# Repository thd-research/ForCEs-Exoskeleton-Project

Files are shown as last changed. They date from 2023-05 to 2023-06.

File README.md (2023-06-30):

# ForCEs-Exoskeleton-Project
Internal Project for the development of a lower-limb active exoskeleton at the Deggendorf Institute of Technology

## Description
The goal of this project is the design and development of an exoskeleton that can be worn with higher levels of acceptance
from patients. In particular, the actuator has a unique four-bar-linkage design, with a conventional belt-and-pulley drive
that allows it to be back driveable. 
The Control System of the exoskeleton relies on the operation of multiple interfaces, mainly a core running on a central processor, 
in this case, a portable Raspberry Pi 4 model B (4 Gb). Arduino Microcontrollers were used for Data Acquisition and ADC.
No specific HMI exists for the use and operation of the exoskeleton. Since an ODrive v3.4 controller is used for the motor control,
most testing and interactions have been achieved through CLI and basic python scripts.
The support structure is created with topology optimization and a prototype was assembled with powder printed parts.
The EMG and Motion Capture Data can be visualized with Software such as EMGandMotionTools by Cometa.

## Structure
- python scripts for:
-- the computation with four-bar-linkage 
-- basic odrive control
- arduino codes for sensor input and control
- cad files for the actuator construction details
- EMG and Motion Capture data 

## Goal of this Repository
To complement the publication titled "Design and Development of a knee rehabilitation exoskeleton with four-bar linkage actuation", so that the experimental trials, as well as results are made available and can be reproduced independently. This work has been completed by several researchers at the DIT and crediting us for any use of the material here would be very much appreciated.
For the image/build file for the Raspberry Pi and additional work with AI Gait recognition, please contact us.

Further organisation information under: https://zaf.th-deg.de/public/project/201

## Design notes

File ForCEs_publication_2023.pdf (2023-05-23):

## Design and Development of a knee rehabilitation exoskeleton with four-bar linkage actuation

C. Y. Aubeeluck¹
, S. Kolbl ¨

1

, D. Dobriborsci¹

and W. Aumer¹

Abstract— In this paper, the design of a lower limb active exoskeleton for rehabilitation purposes is discussed. Active exoskeletons provide the additional required force for motion and gait correction, especially for patients who have suffered from limb impairment. The development was carried out taking into account sensor input for the control system. A Finite-State Machine (FSM) enables the different motions which rely on the data from the torque and acceleration sensors. To replicate the anatomical knee rotation, a four-bar linkage was modelled and integrated in the actuator drive. For this project, a prototype was created using Additive Manufacturing Processes (AMP). The prototype is part of the ’ForCEs’ project at Deggendorf Institute of Technology (DIT) and was tested at an experimental stage for an initial set of results.

I. INTRODUCTION

A variety of conditions results in the impairment of the knee joint, namely chronic illnesses such as cerebral palsy and arthritis, for which the most common treatment is physiotherapy [1]. In modern physiotherapy, active exoskeletons, such as MINDWALKER [2], ReWalk [3], and HAL [4], are mechanized wearables that can be used to assist in rehabilitation. With the use of innovative actuating technologies, and novel material manufacturing processes, researchers have come up with exoskeletons that require the least assistance from medical experts. For rehabilitation, the ‘MINDWALKER’ uses a compact and compliant series elastic actuator with a Brushless DC motor (BLDC). However, despite BLDCs being the most popular actuation choice, bulkiness and low acceptability with patients remain an issue. Another feature is the intent detection for disabled patients. The ‘ReWalk’ exoskeleton consists of a remote control as its input, while the ‘HAL’ by Cyberdyne is the only assistance device with Electromyography (EMG) sensors. While the surface-EMG sensors’ feasibility has been verified, there are still limitations such as noise due to poor adhesion. Furthermore, surface-EMG and EEG electrodes must be adhered to the patient for best results, which drastically decreases their practical usage for daily life applications. Table I summarizes the key elements of the state-of-the-art exoskeletons.

Exoskeleton | Sensing Method | Actuating Method | Joint Type
MINDWALKER ReWalk HAL | IMU Tilt and Torque EMG | linear actuator dc motor dc motor | single-pivot -single-pivot

TABLE I: State of the art exoskeletons (IMU: Inertial Measurement Unit).

1Deggendorf Institute of Technology, TC Cham, 21 Badstraße, 93413 Cham, Germany chandra.aubeeluck@th-deg.de

Based on the review of exoskeletons’ sensors, IMU’s alone serve little purpose in intent detection as they cannot distinguish between the person’s and the actuator’s motion. However, if a secondary or more sensors’ data are combined, an estimation can be obtained. In the ForCEs project [5], a combination of IMU’s and torque sensor has been implemented. This reduces the inconvenience with surface-EMG electrodes. Furthermore, the resistance in motion can be monitored effectively, as opposed to an EMG only solution, where specific muscular activity has to be categorized. At the same time, an adaptive position is generated since the IMU and an angle sensor monitor the leg velocity changes.

By not using a single-pivot joint, the polycentric rotation of the knee, due to the roll and glide motion, has been replicated. One possibility to replicate the anatomical knee rotation is mentioned in [6], where a four-bar linkage approach is introduced. In our case, a similar mechanism has been devised which closer resembles the ligaments inside the knee. These are the Anterior and Posterior Cruciate Ligaments (ACL and PCL) [7]. The femur and tibia bones are the two additional links. The changing centre of rotation is demonstrated in Figure 1. Another key aspect is the use of AMP which improves the form, fit and function of the support structure and actuator. With a backdrivable speed reduction mechanism, the use of a clutch system is eliminated, which makes the actuator lighter.

After a short introduction, the limitations of existing designs are discussed in Section II. Afterwards, the modelling and design of proposed relevant solutions are explained in Section III. Next, in Section IV, an analysis of the implemented solutions is performed and discussed. At the end of Section IV, the obtained results are evaluated. A general emphasis is laid on the overall design concept including the control system, with particular attention to the actuator and four-bar linkage design.

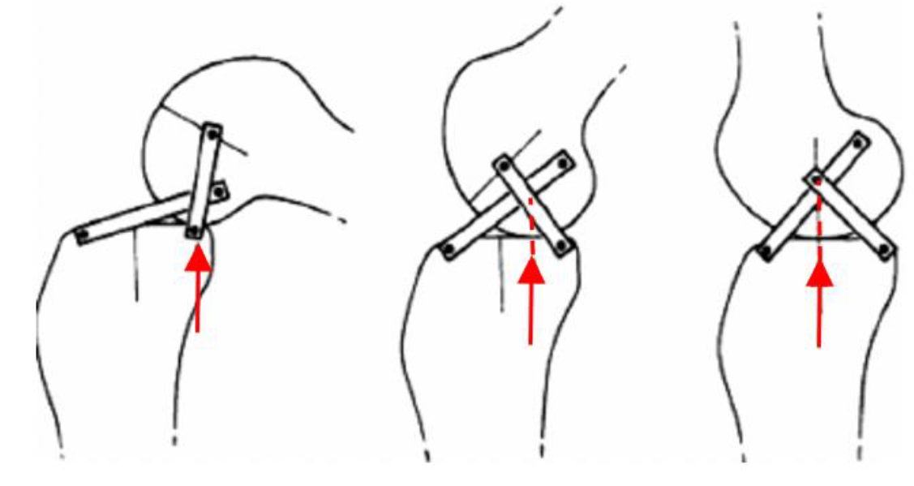
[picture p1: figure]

Fig. 1: Four-bar linkage in the knee. The shifting instantaneous centre of rotation (ICR) is indicated by the red arrow.

II. PROBLEM STATEMENT

The four-bar linkage provides a more adaptive rotation of the actuator joint, given the fact that the axis of rotation of the knee is not the same for every person. A proposed solution is aligning the ICR of the actuator and that of the knee by using parts made by AMP for lightweight supports that conform to the leg profile. An improved control algorithm with torque sensors and IMUs would overcome the current limitations and requirements with existing intent detection means. The extent to which this is resolved is discussed in this paper. While the four-bar linkage provides a more adapted solution, it also introduces the problem of irregular force output in which there is a reduction of up to 40 % of the input force. This is further described in [6]. By knowing the exact torque requirements for each angular position of the knee, the output torque can be adjusted, by varying the torque setpoint. While this is computationally not costly, it still requires an onboard online programming for the estimation of the output torque with respect to the input torques, and gait model torque. A lightweight control structure is thus desired, in which a complete modelling of the exoskeleton is simulated.

III. DESIGN OF CONTROL SYSTEM AND PROTOTYPE

The design for the complete exoskeleton was divided into four parts, namely the structural support, actuators, sensors, and the control system. Using the MSC Adams simulation software [8], a multibody simulation (MBS) at the musculoskeletal level was generated. To obtain the profile of the lower limbs in the sagittal plane, the Opti-Track System was used, where markers placed on the body gives the position of the upper and lower legs. From this, the support structure was developed in several stages starting with a simple element which was enhanced through topology-optimization.

A. Control System Design

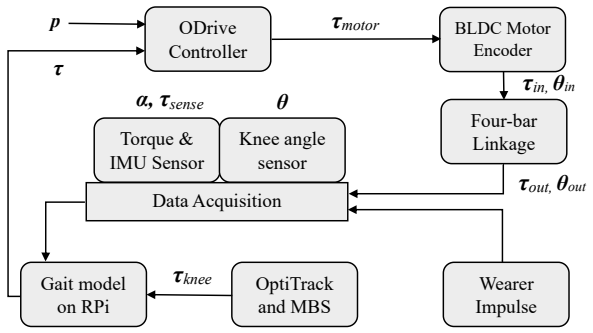
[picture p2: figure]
ODrive Controller; BLDC Motor Encoder; Four-bar Linkage; Wearer Impulse; OptiTrack and MBS; Gait model on RPi; Torque & IMU Sensor; Knee angle sensor; Data Acquisition; τmotor; τin, θin; τout, θout; α, τsense; τknee

Fig. 2: Representation of the exoskeleton Control System.

The components of the control system are illustrated in Figure 2, in which, τ is the torque, α is the tangential acceleration, and θ is the angle of the knee. Further torque variables are τknee, which is the knee required torque according to the gait model and τsense, which is sensed torque. In addition, τmotor is the motor torque, τin is the four-bar linkage input torque at θin and τout is the output torque. The main input variable is designated as the position vector of the motor, p, which is the primary input to a proportional–integral–derivative (PID) controller, where the acceleration is related to the current or torque setpoint, Id of the motor and the voltage Vmotor varies the duty cycle, thus, the motor velocity p˙. This is achieved through the ODrive BLDC Motor Controller [9].

B. Four-bar linkage mechanism

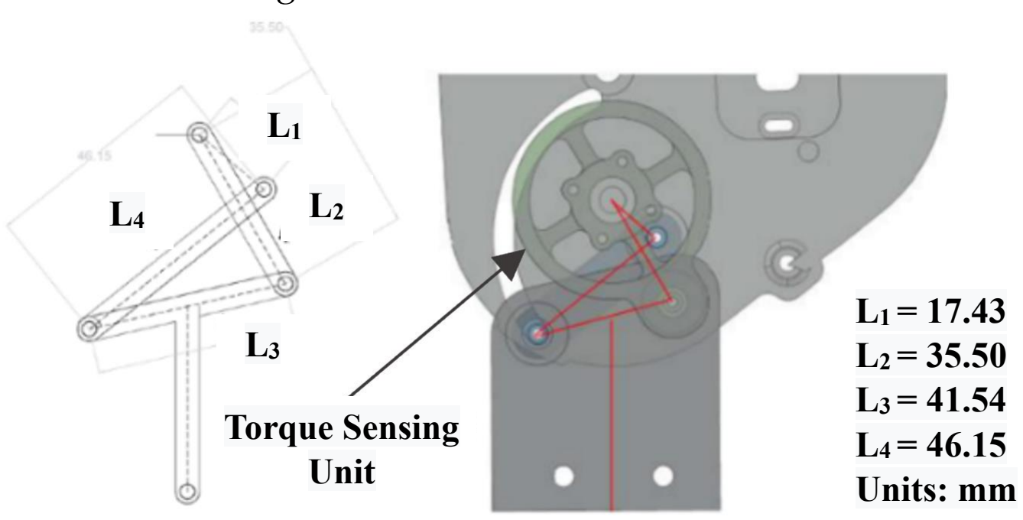
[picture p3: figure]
L1 = 17.43 L2 = 35.50 L3 = 41.54 L4 = 46.15 Units: mm; Torque Sensing Unit

Fig. 3: Four-bar linkage design: dimensions and integration.

The positions and the ratio of the lengths for the knee cruciate ligaments were taken based on the data from [10]. Breaking down the four-bar design, Figure 3 shows the obtained dimensions and design for the four-bar linkage integration. A free-body diagram (FBD) describes the forces in each link, including the relation between the input and output link. The base of the actuator serves as the fixed link L1, which is offset by 40o
to the horizontal. The variations in angular positions are determined by the Freudenstein Equations [11]. The angular range of motion for the input θin, defined by the input or crank link L2, ranges from 20o to 90o
. The output shank connects to link L3 and its rotation θout, relative to the vertical, ranges from 0

o

to 110o
. Link L4
is referred to as the follower, as it determines the path of the output link L3. Link L2 is replaced by a torque sensing element, specifically designed to determine the effective torque input to the four-bar linkage. The forces are distributed in the four links, thus maximizing the permissible peak force acting the torque sensing element, as opposed to the torque sensing element directly transmitting the force to the shank link. In the Autodesk Inventor analysis, the forces are taken from the FBD of the four-bar linkage.

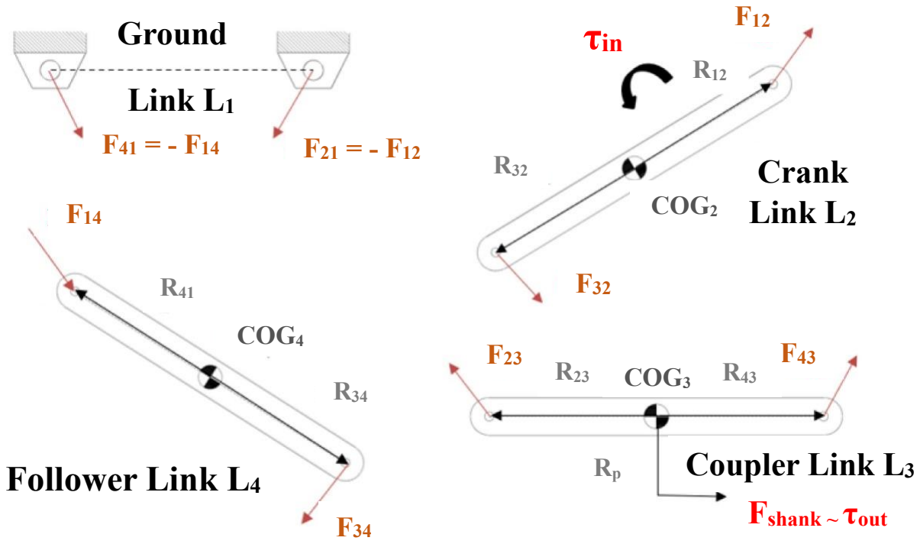
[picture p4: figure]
Ground; Link L1; Follower Link L4; Coupler Link L3; Fshank ~ τout; Crank Link L2 COG2; COG3; COG4; τin

Fig. 4: FBD of four bars for single link analysis.

Figure 4 illustrates each link of the mechanism, clearly showing the fixed Ground L1 and the output force Fshank on the Link L3. The vector quantities Rijxy represent the distance from the Centre of Gravity (COG) and orientation of the links. From the FBD, the forces are resolved at static equilibrium to obtain Equation 1.

Fout = A

−1
- Fin | (1)

where the 8

th element of the (9×1) vector matrix Fout is the force acting on the shank, which is equivalent to the shank torque. Vector matrix Fin contains the elements of the input forces, which in this case is the input torque on the crank link L2 as the 3

rd element. The matrix A is represented in Equation 2. C is the shank length, which is 150 mm. As such, the input and output torques for the linkage are vectors which varies with the angular position. This relation is shown in Figure 5 as the actual torque output with respect

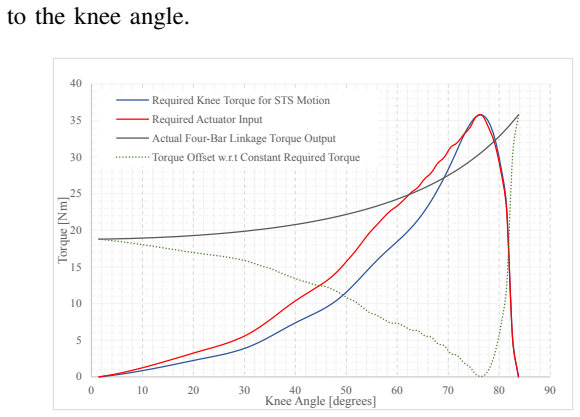
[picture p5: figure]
to the knee angle.; Torque [Nm]; Knee Angle [degrees]; Required Knee Torque for STS Motion; Required Actuator Input; Actual Four-Bar Linkage Torque Output

Torque Offset w.r.t Constant Required Torque

Fig. 5: Torque output from four-bar linkage and offset with respect to Sit-to-Stand (STS) Motion.

From Equation 2, a relation τout = g(τin; θin) is obtained. By iterating the range of torque values with a resolution of 1 Nm, for each knee angle, a difference x exists, which is used in the computation of the actual motor input torque using Equation 3.

τmotor = τout × (

1 + x
100
) | (3)

where
x = τin − τsense | (4)

Equation 4 and its parameters are explained further in section IV. The function g(τin; θin) is dependent on the Freudenstein calculation which is approximated by non-linear curve fitting to obtain

G(θin) = −0.0064θ

2
in + 2.01θin − 37.15 (5)

The required output torque is mapped by the difference e between the output torque τout and the required torque for each gait τknee which varies with the angular positions of the knee. This is represented as the torque offset in Figure
5. The required knee torque τknee is part of the gait model which is represented by a dataset. For this project, the data is retrieved from a CSV file and are operated on as numpy arrays. This allows onboard computation to be performed during the exoskeleton motion. With the required torque for each angular position known, the difference e is determined by first setting the input torque to the peak required torque. In this particular case, the peak required torque is 35 Nm and occurs at knee angle θ = 85o
. The required actuator input τmotor is determined using Equation 3. This is represented in Figure 5 as the required actuator input, where due to the four-bar linkage, in the range 20o < θ < 90o
, the required
actuator torque is decreased to the required knee torque to minimize the torque offset. Within that range, the required torque input is decreased by up to 53 % as shown by the torque offset curve.

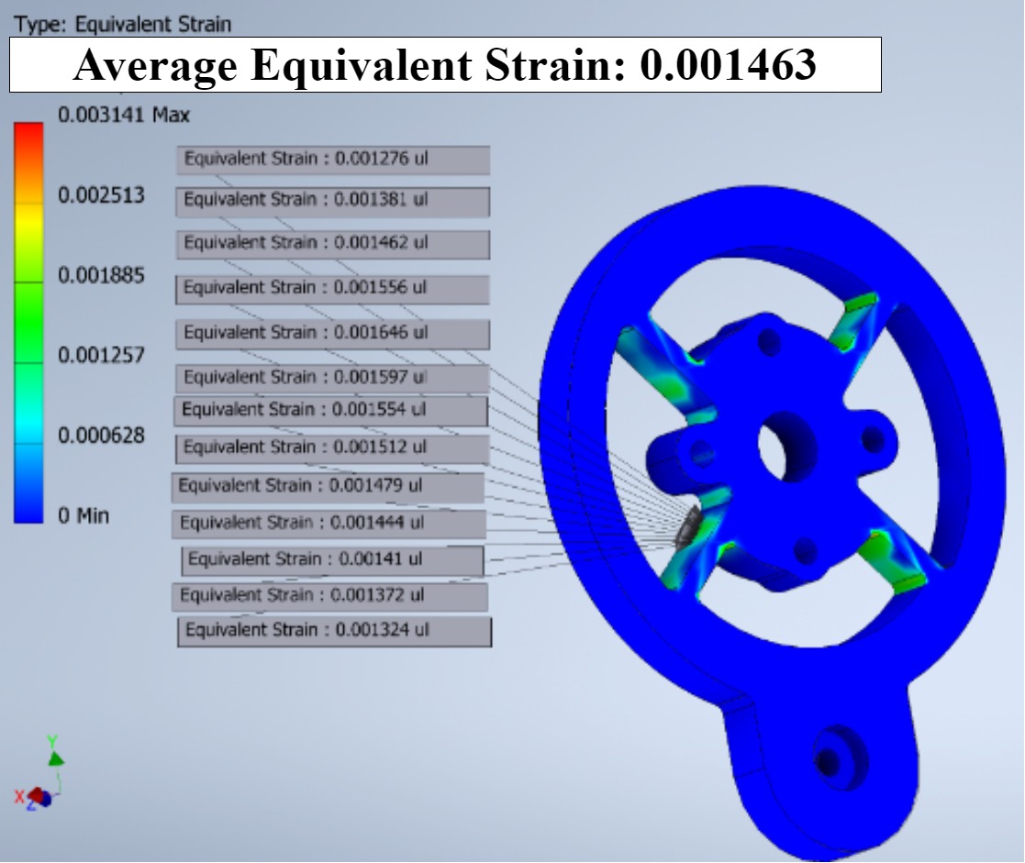
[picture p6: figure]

Fig. 6: FEA analysis on the torque sensing element.

For the torque sensing element, Aluminum 7075 alloy was chosen for its good elastic and yield strength properties. Figure 6 illustrates the Finite Element Analysis (FEA) on the torque sensing element, performed on Autodesk Inventor. Torque increments from 0 to 40 Nm were applied and for each increment, ε was the mean equivalent strain at the position indicated by the green-yellow region on the component. The thickness of that particular region is 2.5 mm and the maximum strain covers an area of 6 mm × 4 mm. An intersecting point where the least allowable safety factor of 2 was selected, and a linear relationship was developed with a slope ms of 0.01214 Nm/ε and intercept Ks of 0.01Nm.

C. Finite State Machine Control

Without registering any muscular activity, intent detection is only possible if the motor is backdrivable and not engaged. Given that the ForCEs exoskeleton is for rehabilitation purposes, it is designed to provide single motion bursts similar to an STS motion. Another type of motion is a swing or stance phase during a walking gait cycle, which last between 15% to 25% of a general walking gait. Thus, an FSM was generated to switch between motor rotation directions, and to switch between control modes of the ODrive controller. The FSM is illustrated in Figure 7. The initial motion detection occurs in state ′S0

′

. States ′

cw′

and ′acw′
correspond to
clockwise (right side flexion) and anticlockwise (right side extension) respectively. If a counter motion is detected while in states ′

cw′

and ′acw′

, this sets the inputs states ′acw′
r

A =

1 | 0 | 1 | 0 | 0 | 0 | 0 | 0 | 0
0 | 1 | 0 | 1 | 0 | 0 | 0 | 0 | 0
−R12y | R12y | −R32y | R32y | 0 | 0 | 0 | 0 | 0
0 | 0 | −1 | 0 | 1 | 0 | 0 | 0 | cos(θ)
0 | 0 | 0 | −1 | 0 | 1 | 0 | 0 | sin(θ)
0 | 0 | R23y | −R23y | −R43y | R43y | 0 | 0 | C
0 | 0 | 0 | 0 | −1 | 0 | 1 | 0 | 0
0 | 0 | 0 | 0 | 0 | −1 | 0 | 1 | 0
0 | 0 | 0 | 0 | R34y | −R34y | −R14y | R14y | 0

(2)

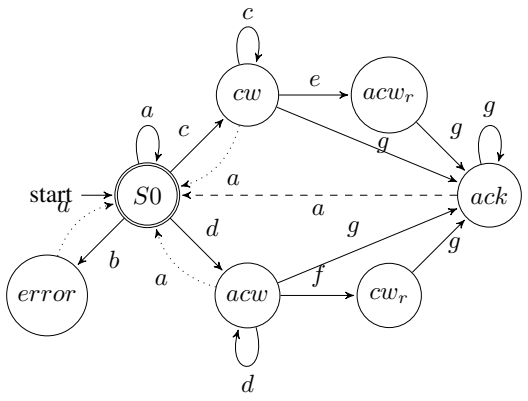
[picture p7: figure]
start; error; acw; acwr; cwr; ack

Fig. 7: FSM of the Control System.

and ′

cw′
r

correspondingly, denoting resistive motion. The exoskeleton control mode is switched between closed-loop filtered position control to closed loop torque control, to eventually an idle state, where the user’s reaction is sensed before applying a further impulse, and repeating the cycle. For each state, the exoskeleton provides an assistive motion that corresponds to the direction registered, with a force proportional to the τmotor torque. That motion is in the form of a linear ramp input to position p of the motor, with a time cycle of 70 ms. The thresholds for torque and acceleration detection are denoted as τt and αt respectively. Input g relates to safety position limits reached, as well as a transition state after a resistive counter motion is detected. The main purpose is to serve as an acknowledgement state before a new intent is detected. The input for each state is detailed in Table II.

Inputs | IMU α | Torque τsense | Motor Torque τmotor
a b c d e f | |α| < αt |α| > αt α > αt α < −αt α << −αt α >> αt | |τ| < τt0 |τ| < τt0 τ < −τt1 τ > τt1 τ > τt2 τ < −τt2 | idle idle idle idle τmotor > τt1 τmotor < −τt1

TABLE II: Input parameters for the FSM.

IV. PROTOTYPE DEVELOPMENT AND EXPERIMENTS

After the design requirements were set and the required simulations performed, a prototype was developed. The three main aspects include the mechanical, electronics and software implementation. In this section, the experimental setups and results are discussed.

A. Setup of the control system
The main architecture comprises of a microcontroller with Analog-to-Digital (ADC) capability for data input, while the gait models were stored on a portable computer such as a Raspberry Pi (RPi), together with the Python scripts for computation. The main communication protocol for the sensor communications are an I²C bus. UART was used between the microcontroller and ODrive controller to transmit the motor position, although the RPi acts as a master node to eliminate time synchronization problem. The setup is illustrated in Figure 8 .

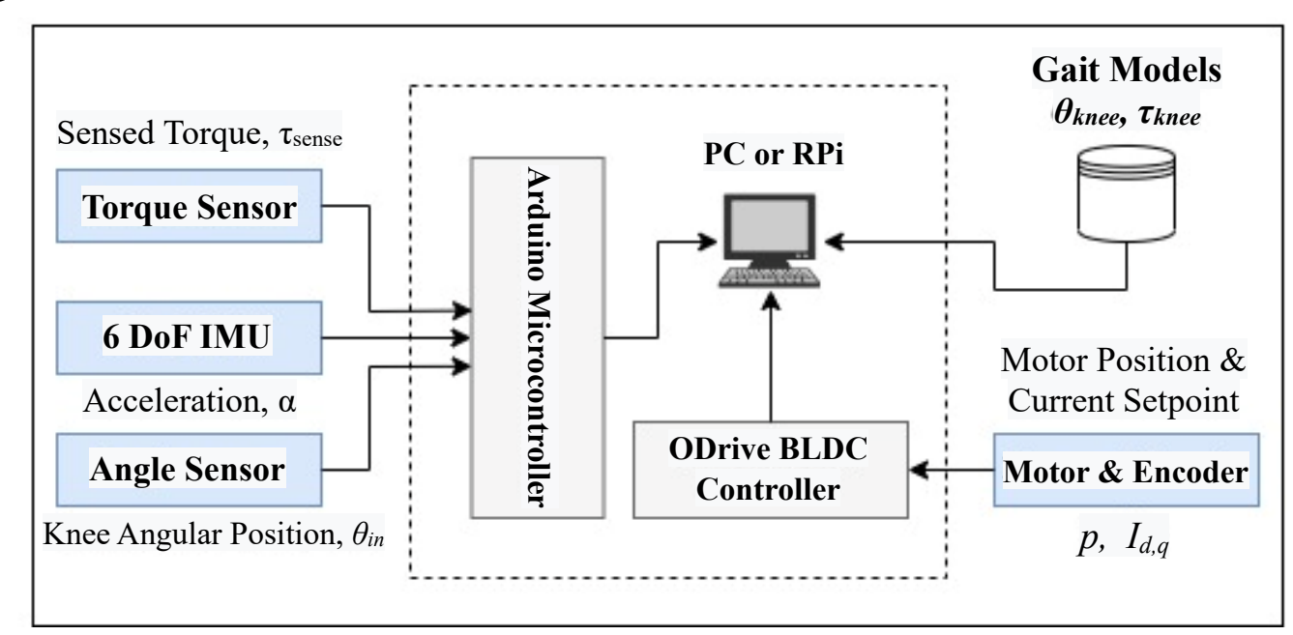
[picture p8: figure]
Torque Sensor; 6 DoF IMU; Angle Sensor; Gait Models; θknee, τknee; Motor Position & Current Setpoint; Motor & Encoder; Arduino Microcontroller; PC or RPi; ODrive BLDC Controller; Sensed Torque, τsense; Acceleration, α; Knee Angular Position, θin

Fig. 8: Data capture interface.

The operation of the FSM is described by the torque and acceleration threshold parameters. Torque thresholds are denoted as vectors and consist of 3 levels – starting from the lowest being the backdrivable torque, the operation torque and resistive torque. In computational representation, the torque values are denoted as their analogue counterpart or voltage level of the sensors. To obtain the actual torque and current values, Equation 4 is further expanded into

x = (Iq × KT × N) − (

4 × Vo
S × Vs

× ms) + Ks (6)

where Iq is the motor current, KT is the torque constant, N is the reduction ratio, S is the strain gauge factor, Vo is the strain voltage, which is equivalent to the torque sensing element voltage, and Vs is the bridge supply voltage. Two reduction ratios have been tested, namely 1:27 and 1:9, each with a BLDC of different torque constants. Furthermore, the third torque threshold is validated by the hall current sensors in the motor controller. From the simulation, the peak strain on the Aluminum 7075 was 0.0016 (1600 µϵ). A 350 Ω linear strain gauge with gauge factor of 2 was used. Amplification was achieved with an INA125P instrumentation amplifier with a gain of 300. Torque and acceleration values were recorded for full flexion and extension motions, and are displayed in Figure 9. The torque values were determined using Equation 6. In comparison with the Table II, the input conditions are confirmed. Counter resistive torques occur at times t = 1.6s, 4s and 4.5s. If the counter resistive torque is not accompanied by a sharp change in acceleration, the counter resistive motion is not registered. Similarly, the same case applies for sharp accelerations while torque values are within the peak thresholds. This occurs when the ’velocity gain’ is lowered to allow a more compliant reaction. The threshold values τt0, τt1 and τt2 are ±2.5 Nm, ±5 Nm and

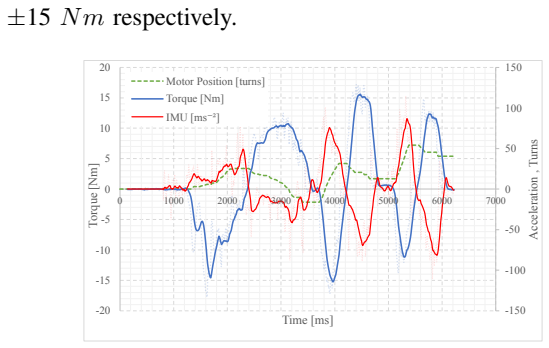
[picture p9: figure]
±15 Nm respectively.; Acceleration , Turns; Torque [Nm]; Time [ms]; Motor Position [turns] Torque [Nm] IMU [ms⁻²]

Fig. 9: Torque and IMU sensor values for intent detection.

The almost linear relation for the acceleration and torque parameters with respect to the knee angle are shown in Figure 10. In this particular case, the shank is accelerated to a constant speed of 60 deg/s. The slight variation of magnitudes less than 2 Nm is the result of the motor cogging torque which also contributes to the backdrivable torque. At a knee angle of 51o
, this results in a shift in the two sensor readings, thus the importance torque-IMU sensor relation

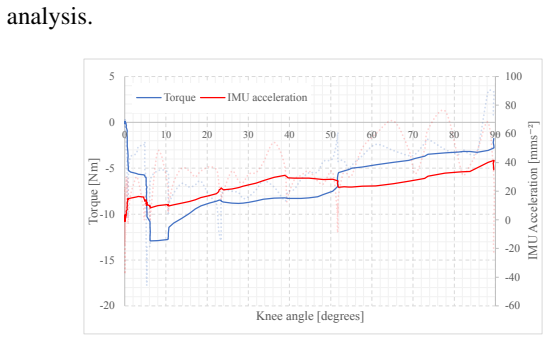
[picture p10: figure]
analysis.; IMU Acceleration [mms; Torque [Nm]; Knee angle [degrees]; Torque; IMU acceleration

Fig. 10: Acceleration and Torque variation with knee angle.

B. Measurement of kinematic and kinetic parameters
A 6 Degree-of-Freedom (DoF) IMU was used as the measurement of the gyroscopic acceleration. It was placed at the length C = 30 mm from the link L3 in the four-bar mechanism. Considering the knee angle θ, the knee angular acceleration is ¨θout = α×C. The thresholds were defined as a binary condition, but there is a direct relation between the gyroscope acceleration and desired motion acceleration. The z-axis value was taken since the IMU sensor lies parallel with the limbs in the sagittal plane, thus only flexion and extension motions are recorded. The measurement of acceleration can be achieved by other devices, such as smartphones. It is further discussed in a separate paper part of the ’ForCEs’ project [12]. An additional element is the 14-bit ‘ams A5048’ angle sensor, through which the position setpoint is confirmed and the angular velocity and acceleration at the crank input L2 of the four-bar is estimated. With onboard programming, the positions of the links are determined based on the angle sensor data and the Freudenstein function G(θin) in Equation 5.
θout = G(θin) | (7)
C. Motion and Intensity Detection
To recognize a motion, the combination of the torque and IMU sensor was analyzed as shown in Table II. From Figure 9, the IMU values within 50±10 mm/s indicate a motion intent, which corresponds to the limits of motion with respect to the backdrivable torque. Acceleration values beyond 50±10 mms⁻¹
indicate an instantaneous deceleration which only occurs when a resistive counter motion is performed. The motor position set point p, measured in revolutions or turns, is equivalent to the knee angle through Equation
7. The difference between pis and pdesired is assigned as pof f set. With the relation G(θin) known, the intensity of the acceleration ¨θout was mapped linearly onto the pof f set value. The aim was to determine the motion within a time less than the general 300 ms human reaction time. With the latency in measurement being less than 100 ms, the actual delay td between a motion and a movement set point being generated was 70 ms, which is well below the 300 ms threshold.
D. Motor Control
The main tuning parameters reached are ’position gain’ = 17 (turn/s)/turn, ’velocity gain’ = 0.165 Nm/(turn/s) and ’velocity integrator gain’ = 0.32 Nm/((turn/s) × s)). These correspond to their PID counterparts in the control structure. The ’CUI AMT-102’ absolute encoder coupled to the motor provides incremental position feedback. Given the known time td, the relation in Equation 7 can be approximated to

pof f set ≈

G⁻¹
(α) × t

2
d × C
N

≈ k × G

−1
(α) (8)

The set position p of the motor is represented in Figure 9. The plateau positions indicate a resistive counter motion where pof f set = 0. Motion is provided via torque bursts between the plateaus. A peak actuating speed of 360 deg/s and a peak torque of 30 Nm at full flexion was achieved for the actuator, which is 30% of the required knee torque for average pace walking [13].

E. Final actuator and structure design
The overall support structure consists of the hip and leg supports, which were 3D-printed with PA 2200 powder. FEA was used as a means of optimizing the form by analyzing the compressive and tensile stresses along the surfaces of the exoskeleton structure. The peak axial and traverse forces that the structure can support are 0.7 kN and 3.8 kN respectively, while the peak moment about the joint is 80 Nm. The overall weight of each side of the exoskeleton is 1.57 kg. The completed prototype is illustrated in Figure 11. An STS motion is demonstrated as it successfully covers a full extension range of 0o

to 100o of the actuator. The adjustable length of the upper leg caters for variable heights of people ranging from 1.7 m to 1.85 m. A safety factor (SF) of 1.6 was achieved for the support limbs, while for the actuator, the SF was 2.

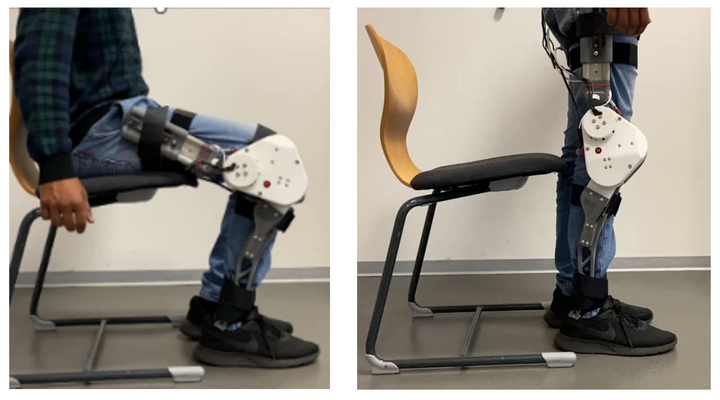
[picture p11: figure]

Fig. 11: Exoskeleton prototype test with an STS motion.

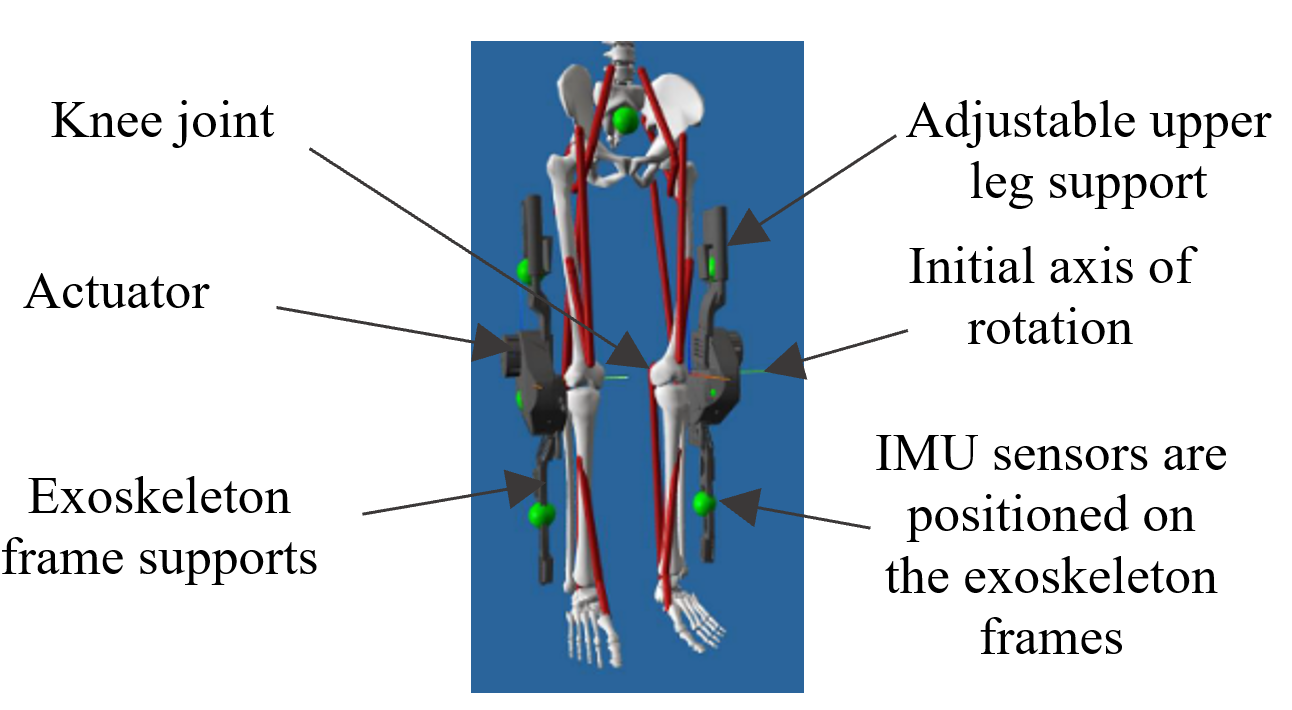
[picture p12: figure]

Fig. 12: MSC Adams representation the musculoskeletal model and the exoskeleton, with axes alignment.

In Figure 12, a MBS taken from an OptiTrack Capture System is displayed. A CAD model of the actuator with four-bar linkage mechanism is included and a clear representation of the alignment of the exoskeleton with the profile of the leg can be observed. In the four-bar linkage, the ICR is determined by the cross-product links L2 and L3. In comparison with the knee model data from [6] and [14], the ICR follows the desired path. Since there is no feasible methodology to determine the precise ICR with respect to a fixed internal point, the initial ICR of the knee was estimated to be used as a reference point. This is represented as the initial axis of rotation at knee extension in Figure 12.

V. CONCLUSIONS
A prototype for the ’ForCEs’ exoskeleton was developed that could serve the purpose of rehabilitation for patients with mild knee impairment. A unique design for the integration of the four-bar linkage which replicates the interior of the knee joint ligaments was proposed and assembled. This was tested successfully in both a simulation and on a prototype. Through topology optimization, an exoskeleton frame that could support direct forces up high compression axial forces and torques up to 30 Nm, was developed with additive manufacturing. Additionally, it provides a way to facilitate the development of personalized exoskeletons. The finite state algorithm operating with two sensors provide a new method of intent detection that does not rely on muscular activity which can be further improved with a trained AI model.

ACKNOWLEDGMENT
The ForCEs Exoskeleton project was a joint internal project between three campuses of the Deggendorf Institute of Technology in Bavaria, Germany. The partners include Technology Campus (TC) Cham, TC Hutthurm and TC Freyung.

REFERENCES

[1] P. Lum, D. Reinkensmeyer, R. Mahoney, W. Z. Rymer, and C. Burgar, “Robotic devices for movement therapy after stroke: current status and challenges to clinical acceptance,” Topics in stroke rehabilitation, vol. 8, no. 4, pp. 40–53, 2002.
[2] S. Wang, L. Wang, C. Meijneke, E. van Asseldonk, T. Hoellinger,
G. Cheron, Y. Ivanenko, V. La Scaleia, F. Sylos-Labini, M. Molinari,
F. Tamburella, I. Pisotta, F. Thorsteinsson, M. Ilzkovitz, J. Gancet,
Y. Nevatia, R. Hauffe, F. Zanow, and H. van der Kooij, “Design and control of the mindwalker exoskeleton,” IEEE Transactions on Neural Systems and Rehabilitation Engineering, vol. 23, no. 2, pp. 277–286, 2015.
[3] A. Esquenazi, M. Talaty, A. Packel, and M. Saulino, “The ReWalk powered exoskeleton to restore ambulatory function to individuals with thoracic-level motor-complete spinal cord injury,” American Journal of Physical Medicine &amp Rehabilitation, vol. 91, no. 11, pp. 911–921, Nov. 2012.
[4] S. Ezaki, H. Kadone, S. Kubota, T. Abe, Y. Shimizu, C. K. Tan, K. Miura, Y. Hada, Y. Sankai, M. Koda, K. Suzuki, and
M. Yamazaki, “Analysis of gait motion changes by intervention using robot suit hybrid assistive limb (HAL) in myelopathy patients after decompression surgery for ossification of posterior longitudinal ligament,” Frontiers in Neurorobotics, vol. 15, Mar. 2021. [Online]. Available: https://doi.org/10.3389/fnbot.2021.650118
[5] C. Aubeeluck, “’forces’ exoskeleton project,” https://github.com/thdresearch/ForCEs-Exoskeleton-Project, 2023.
[6] J.-H. Kim, M. Shim, D. H. Ahn, B. J. Son, S.-Y. Kim, D. Y. Kim,
Y. S. Baek, and B.-K. Cho, “Design of a knee exoskeleton using foot pressure and knee torque sensors,” International Journal of Advanced Robotic Systems, vol. 12, no. 8, p. 112, 2015.
[7] D. Saldias, D. Martins, C. de Mello Roesler, F. da Silva Rosa, and A. Ocampo More, “Modeling of human knee joint in sagittal ´ plane considering elastic behavior of cruciate ligaments,” in 22nd International Congress of Mechanical Engineering, 2013.
[8] Hexagon, | “Adams.” | [Online]. | Available:
https://hexagon.com/products/product-groups/computer-aidedengineering-software/adams
[9] O. Weigl, “Odrive.” [Online]. Available: https://odriverobotics.com/
[10] F. D. Ruiz-D´ıaz, A. Altamirano-Altamirano, and G. Valentino-Orozco, “External knee prosthesis with four bar linkage mechanism,” in 2016 13th International Conference on Electrical Engineering, Computing Science and Automatic Control (CCE). IEEE, 2016, pp. 1–6.
[11] F. Freudenstein, “An analytical approach to the design of four-link mechanisms,” Transactions of the American Society of Mechanical Engineers, vol. 76, no. 3, pp. 483–489, 1954.
[12] S. Kirmess, C. Sigl, and W. Dorner, “Analysing movement patterns from smartphones for the training of exoskeletons,” in 2022 12th International Conference on Advanced Computer Information Technologies (ACIT). IEEE, 2022, pp. 472–475.
[13] G. E. Caldwell, W. B. Adams III, and M. R. Whetstone, “Torque/velocity properties of human knee muscles: peak and anglespecific estimates,” Canadian journal of applied physiology, vol. 18, no. 3, pp. 274–290, 1993.
[14] T. Besier, M. Schneider, N. Rooks, and M. Kazemi, “Model specifications abi–open knee data.”

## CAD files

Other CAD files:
python_scripts/Calculations/four bar linkage and freudenstein.dwg

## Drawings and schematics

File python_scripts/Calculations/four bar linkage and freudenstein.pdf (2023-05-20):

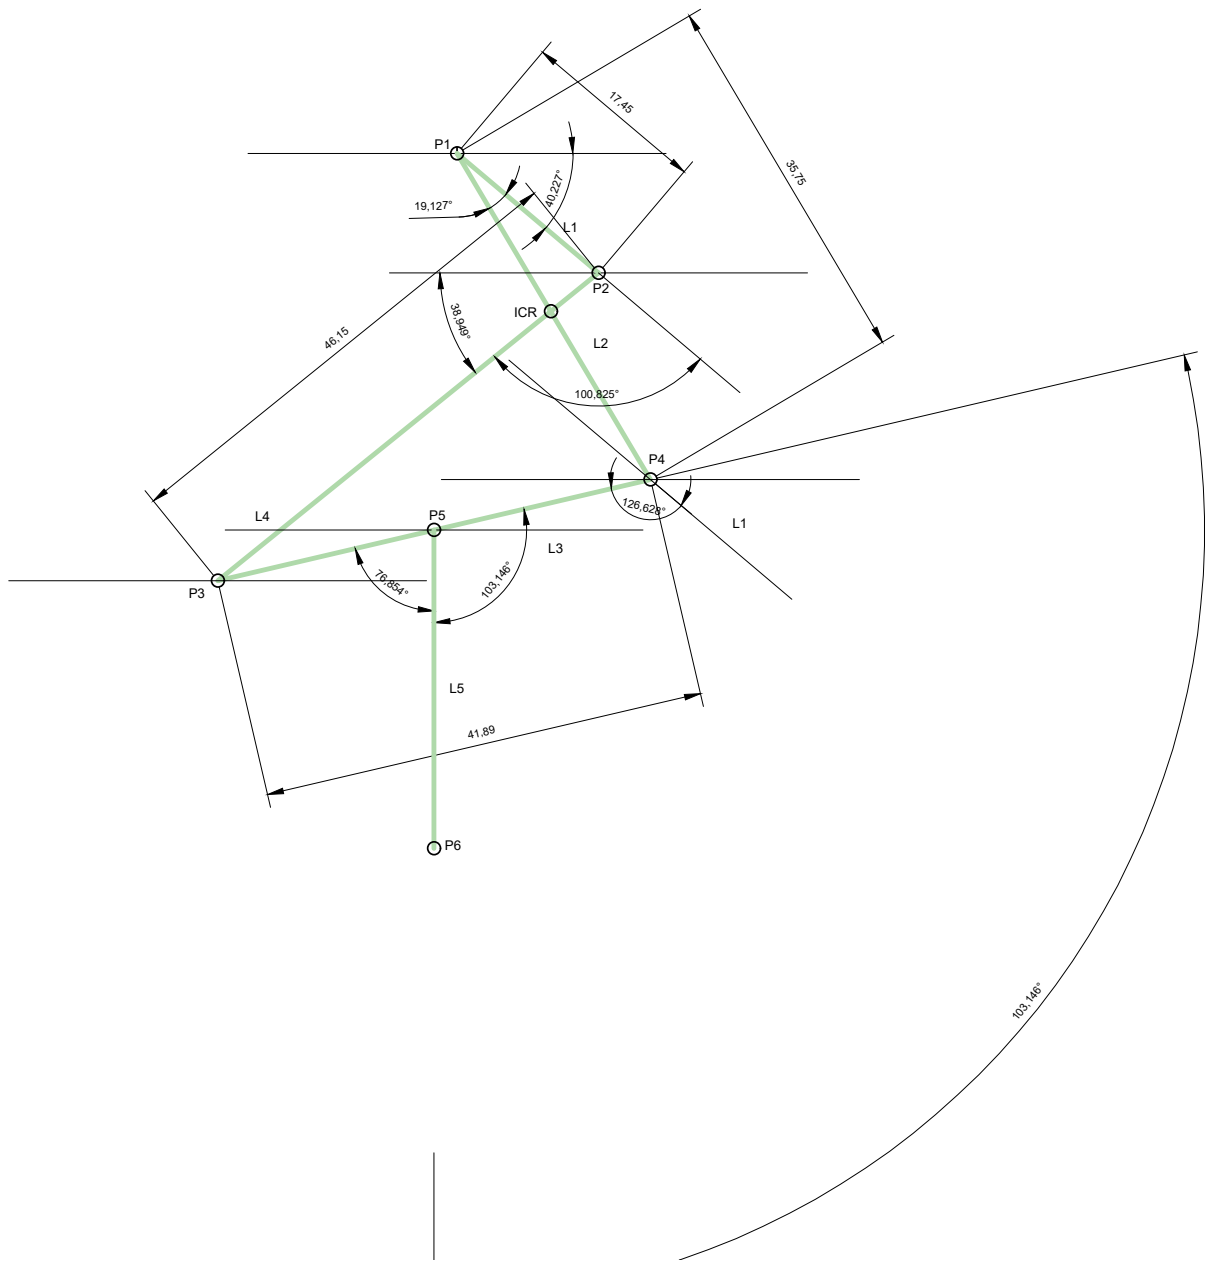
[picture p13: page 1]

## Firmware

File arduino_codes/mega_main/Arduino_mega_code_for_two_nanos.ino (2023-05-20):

/***** Arduino Mega *****/
#include <HardwareSerial.h>
#include <SoftwareSerial.h>
#include <DHT.h>

#include <MovingAverageFloat.h>

// for imuo values
MovingAverageFloat <16> filter0;
//for imu1 values
MovingAverageFloat <16> filter1;

//right leg 0
float p0_max = 5;
float p0_min = -0.5;

//left leg 1
float p1_max = 7.4;
float p1_min = 1.1;

int tavg = 10; 
int data0 = 1000; //arbitrary huge value for error detection
int data02 = 1000;

#include <ODriveArduino.h>
// Printing with stream operator helper functions
template<class T> inline Print& operator <<(Print &obj,     T arg) { obj.print(arg);    return obj; }
template<>        inline Print& operator <<(Print &obj, float arg) { obj.print(arg, 4); return obj; }

////////////////////////////////
// Set up serial pins to the ODrive
////////////////////////////////

// Arduino Mega or Due - Serial1
// pin 19: RX - connect to ODrive TX
// pin 18: TX - connect to ODrive RX
// See https://www.arduino.cc/reference/en/language/functions/communication/serial/ for other options
HardwareSerial& odrive_serial = Serial1;

// ODrive object
ODriveArduino odrive(odrive_serial);

float enc_val;
#define joyX A7
#define joyY A7

int relay = 11;

float m,k;

int a_max = 120;
int a_min = 0;

char recieved_data[100]; //Initialized variable to store recieved data

char recieved_data2[100]; //Initialized variable to store recieved data

char *temPtr; // pointer to take the data and to increment after (,)
int angle_value;
int imu1_value;

char *temPtr2; // pointer to take the data and to increment after (,)
int angle_value2;
int imu1_value2;

void setup() 
{

  odrive_serial.begin(115200);

  
  int requested_state;
int motornum = '0'-'0';
  requested_state = AXIS_STATE_CLOSED_LOOP_CONTROL;
  Serial << "Axis" << '0' << ": Requesting state " << requested_state << '\n';
  if(!odrive.run_state(motornum, requested_state, false /*don't wait*/)) return;

odrive_serial << "w axis" << 0 << ".controller.config.input_filter_bandwidth " << 5.0f << '\n';

odrive_serial << "w axis" << 0 << ".controller.config.input_mode " << 3 << '\n';
  
  // Begin the Serial at 9600 Baud
  Serial.begin(9600);
  Serial3.begin(9600); // Using UART channel 3 
 Serial2.begin(9600); // Using UART channel 2
  while (!Serial3);
  while (!Serial2);


}

void loop() 
{
//sensor_data();

int I = 10;
for (int i = 0; i < I; i++)
{

data0 = analogRead(A0);
filter0.add(data0);
delayMicroseconds(tavg);

}
//fetch averaged value:
data0 = filter0.get();
Serial.print(data0);Serial.print("\t");
//Serial.print(analogRead(A7));Serial.print("\t");

sensor_data2();

int  xValue = analogRead(joyX);
int  yValue = analogRead(joyY);

  Serial.flush();
//  char c = Serial.read();
//Serial.println(c);
m = (p0_max - p0_min)/1023;
k = p0_min;

float p = (m*xValue) + k;




odrive.SetPosition(0,p);                                      
delay(5);

/*
if(yValue>=0 && yValue<=249)
{
  //stay still - motor doesn't turn
 enc_val = encoder();
 odrive.SetPosition(1,enc_val);
 if(xValue<=490) //turn motor in negative direction (--)
{

enc_val = encoder();
for (float p=enc_val; p>p0_min ;p-=0.1){
  sensor_data();
  xValue = analogRead(joyX);
  yValue = analogRead(joyY);
  if(xValue>490){
  break;
}
odrive.SetPosition(1,p);
delay(5);
}
}
}

else if(yValue>=250) //turn motor in positive direction (++)
{


enc_val = encoder();
for (float p=enc_val; p<p0_max ; p+=0.1){
  sensor_data();
  xValue = analogRead(joyX);
  yValue = analogRead(joyY);
  if(yValue<250){
    //enc_val=encoder();
  break;
}
odrive.SetPosition(1,p);
delay(5);
}
} */




  
   }


  
float encoder()
{
  odrive_serial << "r axis" << 1 << ".encoder.pos_estimate\n";  
String enc = odrive_serial.readStringUntil('\r');
enc = enc.substring(0,6);
float enc2=enc.toFloat();



return enc2;

//string to int:
//enc.replace(".","");
//int enc2=enc.toInt();
//float enc3=float(enc2);
//enc3=enc3/1000;
}


 //left leg
void sensor_data()
{
   byte n = Serial3.available();
    if (n != 0)
  {
  byte n = Serial3.available();
    if (n != 0)
  {
    byte m = Serial3.readBytesUntil('\n', recieved_data, 200);
    recieved_data[m] = '\0';  //null-byte
    // Serial.println(myData);
    //------------------------------
    unsigned int temp_value = strtoul(recieved_data, &temPtr, 10); // Temperature sensor Value first one to send 
    
    unsigned int s2 = strtoul(temPtr + 1, &temPtr, 10); // angle sensor second one to send 
    angle_value = s2; // /100.0; // to take it here with decimal points 
    int s3 = strtoul(temPtr + 1, &temPtr, 10); // IMU value of the sensor it is the third one 
   
   imu1_value = s3; // /100.0;
  /***** if you want to Add any sensors to nano and get the values seperatly in the mega to use them 
  but add in the nano a (,) to distinquish between the values *****/
  
  /*****
  unsigned int s4 = strtoul(temPtr + 1, &temPtr, 10);
    unsigned int s5 = strtoul(temPtr + 1, &temPtr, 10);
    unsigned int s6 = strtoul(temPtr + 1, &temPtr, 10);
    unsigned int s7 = strtoul(temPtr + 1, &temPtr, 10);
    unsigned int s8 = strtoul(temPtr + 1, &temPtr, 10);
  //mapped angle value:
  
  *****/

  int mapped_angle = map(angle_value,4189,7800, 80,0);
  
    //Printing the values of the sensors 


  if(temp_value!=0){
   // Serial. print(analogRead(A7)); Serial.print("\t");
 //   Serial. print(temp_value); Serial.print("\t");
   // Serial. print(mapped_angle); Serial.print("\t");
   // Serial. print(encoder()); Serial.print("\t");
    
    //Serial. print(imu1_value+10);Serial.print("\t");
    //Serial.println();
  }
}
  }


  
}





//right leg

void sensor_data2()
{
   byte n2 = Serial2.available();
    if (n2 != 0)
  {
  byte n2 = Serial2.available();
    if (n2 != 0)
  {
    byte m2 = Serial2.readBytesUntil('\n', recieved_data2, 200);
    recieved_data2[m2] = '\0';  //null-byte
    // Serial.println(myData);
    //------------------------------
    unsigned int temp_value2 = strtoul(recieved_data2, &temPtr2, 10); // Temperature sensor Value first one to send 
    
    unsigned int s22 = strtoul(temPtr2 + 1, &temPtr2, 10); // angle sensor second one to send 
    angle_value2 = s22; // /100.0; // to take it here with decimal points 
    int s32 = strtoul(temPtr2 + 1, &temPtr2, 10); // IMU value of the sensor it is the third one 
   
   imu1_value2 = s32; // /100.0;
  /***** if you want to Add any sensors to nano and get the values seperatly in the mega to use them 
  but add in the nano a (,) to distinquish between the values *****/
int s42 = strtoul(temPtr2 + 1, &temPtr2, 10); // gz of IMU value of the sensor it is the fourth one 
int gz_value = s42;

  
  /*****
  unsigned int s4 = strtoul(temPtr + 1, &temPtr, 10);
    unsigned int s5 = strtoul(temPtr + 1, &temPtr, 10);
    unsigned int s6 = strtoul(temPtr + 1, &temPtr, 10);
    unsigned int s7 = strtoul(temPtr + 1, &temPtr, 10);
    unsigned int s8 = strtoul(temPtr + 1, &temPtr, 10);
  //mapped angle value:
  
  *****/

  int mapped_angle2 = map(angle_value2,4490,7741, 0,80);
  


  if(temp_value2!=0){
   // Serial. print(analogRead(A7)); Serial.print("\t");
 //   Serial. print(temp_value); Serial.print("\t");
   // Serial. print(mapped_angle); Serial.print("\t");
   // Serial. print(encoder()); Serial.print("\t");
   // Serial.print(data02); Serial.print("\t");
  //  Serial.print(temp_value2);Serial.print("\t");
    Serial.print(s22);Serial.print("\t");
    Serial.print(s32);Serial.print("\t");
    Serial.println(s42);
  }
}
  }
}

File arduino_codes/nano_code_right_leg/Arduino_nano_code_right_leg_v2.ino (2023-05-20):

#include <Wire.h>
#include <Adafruit_Sensor.h>
#include <Adafruit_BNO055.h>
#include <utility/imumaths.h>

/* Set the delay between fresh samples */
#define BNO055_SAMPLERATE_DELAY_MS (50)

// Check I2C device address and correct line below (by default address is 0x29 or 0x28)
//                                id, address
Adafruit_BNO055 bno = Adafruit_BNO055(-1, 0x28);

/***** LSM6DSO32 *****/
#include <Adafruit_LSM6DSO32.h>
#include <Wire.h>

/*****Moving Average function*****/
#include <MovingAverageFloat.h>

/***** For IMUo values*****/
MovingAverageFloat <16> filter0;

/*****Moving average time interval in microseconds*****/
int tavg_imu = 10; 

/*****For MUX*****/
//uint8_t t;
uint8_t addr;

//Testing two sensors connected to MUX: (Create a separate instance for each)
Adafruit_LSM6DSO32 dso32; //@ 0x6A
Adafruit_LSM6DSO32 dso32_2; //@ 0x6A

#define TCAADDR 0x70

void tcaselect (uint8_t i)
{
if (i > 7) return;

Wire.beginTransmission(TCAADDR);
Wire.write(1 << i);
Wire.endTransmission();
}

//gyro values:
float imu0_gz;
float imu1_gz;

/***** TEMPERATURE SENSOR*****/
#include <DHT.h>
#define DHTPIN 7     // pin we're connected to
#define DHTTYPE DHT22   // DHT 22 
DHT dht(DHTPIN, DHTTYPE); // Initialize DHT sensor for normal 16mhz Arduino

int temperature; //Temperature  value

/*****ANGLE SENSOR*****/
#include <AS5048A.h>
int angle_value;
AS5048A angleSensor(10, true);
char values_of_angle[10];

char values_of_imu[10];

void setup() 
{
Serial.begin(9600);

Wire.begin();

delay(100);

dht.begin(); //Temperature sensor intilliaze 
angleSensor.begin(); //Angle sensor intilliaze

/* Initialise the bn055 sensor */
  if (!bno.begin())
  {
    /* There was a problem detecting the BNO055 ... check your connections */
    Serial.print("Ooops, no BNO055 detected ... Check your wiring or I2C ADDR!");
    while (1);
  }




}



void loop() 
{
temperature= dht.readTemperature(); // INTEGEAR VALUE

angle_value = angleSensor.getRawRotation();

//float imu0_val = imu0();


  //could add VECTOR_ACCELEROMETER, VECTOR_MAGNETOMETER,VECTOR_GRAVITY...
  sensors_event_t orientationData , angVelocityData , linearAccelData, magnetometerData, accelerometerData, gravityData;
  bno.getEvent(&orientationData, Adafruit_BNO055::VECTOR_EULER);
  bno.getEvent(&angVelocityData, Adafruit_BNO055::VECTOR_GYROSCOPE);
  bno.getEvent(&linearAccelData, Adafruit_BNO055::VECTOR_LINEARACCEL);
  bno.getEvent(&magnetometerData, Adafruit_BNO055::VECTOR_MAGNETOMETER);
  bno.getEvent(&accelerometerData, Adafruit_BNO055::VECTOR_ACCELEROMETER);
  bno.getEvent(&gravityData, Adafruit_BNO055::VECTOR_GRAVITY);


imu::Vector<3> acceleration = bno.getVector(Adafruit_BNO055::VECTOR_ACCELEROMETER);
imu::Vector<3> gyro = bno.getVector(Adafruit_BNO055::VECTOR_GYROSCOPE);

float gx,gy,gz;
float ax,ay,az;

 // gz = printEvent2(&angVelocityData);

gz = printEvent2(&accelerometerData);
  ax = printEvent(&accelerometerData);


int axx = ax*100;
int gzz = gz*100;

Serial.print(temperature);Serial.print(",");
Serial.print(angle_value);Serial.print(",");
Serial.print(axx);Serial.print(",");
Serial.println(gzz);


      delay(BNO055_SAMPLERATE_DELAY_MS);

}



float printEvent(sensors_event_t* event) {
  double x = -1000000, y = -1000000 , z = -1000000; //dumb values, easy to spot problem
  if (event->type == SENSOR_TYPE_ACCELEROMETER) {
    //Serial.print("Accl:");
    //x = event->acceleration.x;
    x = event->acceleration.x;
  //  y = event->acceleration.y;
  //  z = event->acceleration.z;
  }




  else {
    Serial.print("Unk:");
  }

  //Serial.print("\tx= ");
 // Serial.print(x);
return x;
}







float printEvent2(sensors_event_t* event) {
  double x = -1000000, y = -1000000 , z = -1000000; //dumb values, easy to spot problem



  if (event->type == SENSOR_TYPE_GYROSCOPE) {
   // Serial.print("Gyro:");
  //  x = event->gyro.x;
  //  y = event->gyro.y;
   
    
    z = event->gyro.z;

 //y = event->acceleration.y;
    
  }


   else if (event->type == SENSOR_TYPE_ACCELEROMETER) {
    //Serial.print("Accl:");
    //x = event->acceleration.x;
    y = event->acceleration.y;
  //  y = event->acceleration.y;
  //  z = event->acceleration.z;
  }



  else {
    Serial.print("Unk:");
  }

return y;
}

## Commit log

2023-05-20 python scripts
    [four bar linkage and freudenstein.dwg]
2023-05-20 arduino files
2023-06-30 emg and optitrack motion capture data
    Data capture performed with the exoskeleton with the OptiTrack System, together with EMG data for the lower and upper leg muscles.
    [EMG_Aufstehen_Take3_2023-02-09 10.42.24 AM.csv, EMG_Aufstehen_Take5_2023-02-09 10.43.45 AM.csv, EMG_Gehen_Take10_2023-02-09 10.51.25 AM.csv, EMG_Gehen_Take7_20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]
